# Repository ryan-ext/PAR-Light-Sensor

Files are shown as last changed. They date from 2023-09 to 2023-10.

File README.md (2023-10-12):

# PAR-Light-Sensor

This project uses a AS7341 light sensor as a low cost alternative to a quantum sensor to make a Photosynthetic Photon Flux Density (PPFD) measurement. This sensor does not have a flat sensitivity throughout the 400-700 nm range, but has seven measurement channels spanning the range. As such, it is most accurate when used with the specific type of light or fixture for which is has been calibrated.

A description of the work to develop and test the sensor can be found in this article. 
https://www.ctahr.hawaii.edu/oc/freepubs/pdf/FST-68.pdf

**Background**
The range of light wavelengths which is useful to plants is referred to as Photosynthetically Active Radiation (PAR) range. PAR is measured with a quantum light meter which counts the number of photons, or light particles, within the PAR range hitting the sensor and is commonly expressed in the units of micromoles per square meter per second (µmol/m2/s). This quantity is referred to as the Photosynthetic Photon Flux Density (PPFD). A mole (mol) is simply a unit to count the photons, and there are one million micromoles (µmol) in each mole.

The PPFD, or light intensity, is used to determine the total light provided to plants over the course of a day. This parameter is the Daily Light Integral (DLI) and is expressed in units of mol/m2/d. The DLI is calculated by multiplying the PPFD by the duration of time in hours (T) that the plant receives light and then performing a unit conversion by multiplying by a factor of 3600 (seconds in one hour) and dividing by a million to convert from units of micromoles to moles. As an example, hydroponic lettuce requires 14 - 17 mol/m2 PAR each day. Over a 16-hour light period, the PPFD would need to fall between 243 - 295 µmol/m2/s. The DLI determination for an indoor operation using grow lights is very simple since the light intensity does not change over the course of the day.

**AS7341 Sensor**
The custom PPFD meter was designed to be cost effective and simple to build and assemble (Figure 3). The two main components are the light sensor and a microcontroller that communicates with the sensor and displays readings to the user. The sensor is positioned at the top of a 3D printed case that can be handheld or mounted to a tripod or articulating arm with a ¼”-20 threaded mount. The Adafruit ESP32 S2 TFT Feather microcontroller selected can send readings to a computer through a USB connection or wirelessly over WiFi and Bluetooth and has a built-in LCD screen to display measurements in real time to the user. The connection to the sensor also does not require soldering. Other components include a cable connecting the sensor and microcontroller, USB cable for data transfer and to upload the code to run the microcontroller, mounting screws, and an acrylic diffuser for the sensor.

The three-part case was 3D printed with a filament deposition printer (Pulse XE). The main body incorporates mounting holes to secure the microcontroller and sensor to the case. The 3D printed cap contains a pocket to hold a circular light diffuser that scatters light from oblique sources, or extreme angles, which might otherwise cast a shadow on the sensor from the edges of the sensor chip package. A rectangular plate covers the main compartment of the case to protect the microcontroller. Metric M2.3, 2.5 or 2.6 self-tapping screws attach the sensor, microcontroller, cap, and cover plate to the main body. 



**PPFD Calibration**
The raw photon counts of the sensors were converted to actual PPFD values through a calibration process that used a quantum meter (Spectrum Technologies Solar Electric Quantum Meter #3415FSE) as the reference for PPFD. This quantum meter has settings for electric and solar light. The electric light setting was used with all grow lights regardless of type. A mounting bracket kept the angle, height, and position of the reference meter and light sensors consistent to ensure that all devices were exposed to the same light conditions when under an LED grow light. A range of PPFD through a maximum of 700 µmol/m2/s, typical for indoor agriculture, were produced by changing the light intensity, height of the grow light, and horizontal position under the light. Readings from the reference meter and AS7341 were recorded when each was centered on nine positions designated on a grid below the light fixture.

Readings from both the reference meter and AS7341 were observed to increase consistently as the light intensity was raised. This type of proportional or linear relationship shown in Figure 8 for full spectrum LED indicates that the conversion of the photon count to a PPFD reading can accomplished with the formula for a straight line. The PPFD value is calculated by multiplying the sensor photon count by the slope of the line and then adding that product to the offset or y-intercept value. For example, the raw photon count of the AS7341 must be divided by 32.75. The resulting value is a PPFD reading in units of µmol/m2/s. In this particular calibration result, there is no significant offset between the sensor output and quantum meter reading. 



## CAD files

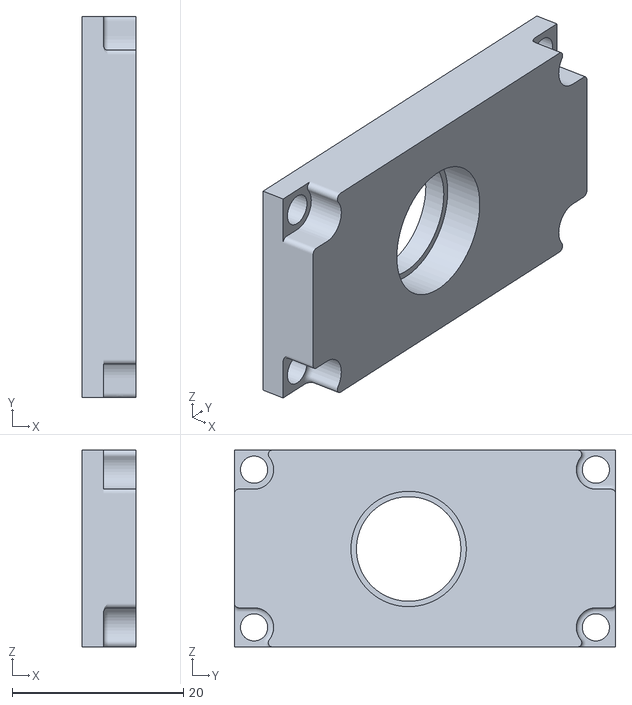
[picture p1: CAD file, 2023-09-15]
Diffuser_Cap_v10.stl
6.35 x 44.5 x 23.0

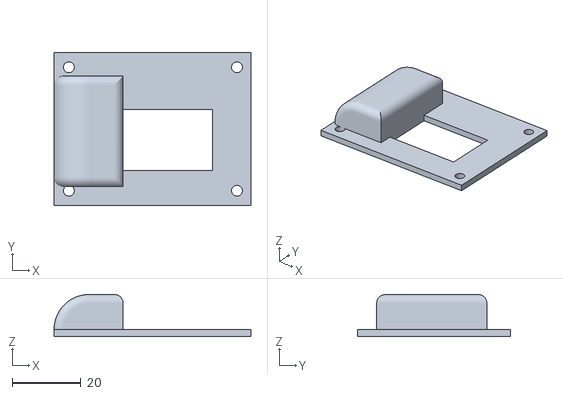
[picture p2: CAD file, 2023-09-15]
Cover_v5.stl
57.2 x 44.5 x 12.2

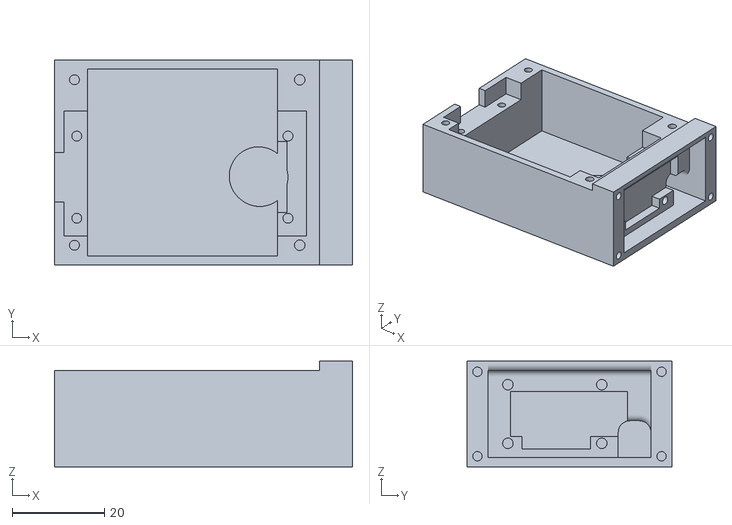
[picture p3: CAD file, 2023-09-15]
Case_v16.stl
64.5 x 44.5 x 22.9
